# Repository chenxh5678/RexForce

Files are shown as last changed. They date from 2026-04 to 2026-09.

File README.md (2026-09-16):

# RexForce测力主板开发说明文档

>建议用电脑浏览器打开此文档，方便下载文件

## 目录
1. [设备概述](#1-设备概述)
2. [测力传感器接线](#2-测力传感器接线)
3. [电池说明](#3-电池说明)
4. [设备操作与指示](#4-设备操作与指示)
5. [连接方式](#5-连接方式)
6. [通信协议](#6-通信协议)
7. [客户端开发指南](#7-客户端开发指南)
8. [归零校准操作](#8-归零校准操作)
9. [注意事项](#9-注意事项)
10. [主板尺寸图](#10-主板尺寸图)
11. [应用程序](#11-应用程序)
12. [示例：测力台采购组装教程](测力台采购装配/README.md)
13. [成品测力台、测力计购买](#13-成品测力台测力计购买)
---

## 1. 设备概述
### 1.1 设备定义
RexForce 测力主板是一款用于测力采集的控制主板，可连接各类测力传感器，用于制造运动测力台、肌力测试仪、力量评估设备、康复评估设备、平衡测试平台等运动与康复类设备，以及工业测力计、拉压力测试机、吊装测力装置、工装夹具测力装置、智能称重终端等工业类设备。

### 1.2 功能说明
设备支持 **BLE 蓝牙** 连接和**额外串口模块**有线连接，支持手机、平板、带蓝牙功能的电脑等客户端接入，并以 **1000 Hz** 采样速率实时输出重量数据，适用于测力采集、数据显示与无线传输等应用场景。

### 1.3 工作模式
设备支持以下工作模式：
- **单机模式**：仅发送主设备重量数据。
- **双机模式**：将有线连接的主设备与副设备的重量数据合并发送。

### 1.4 主板参数
| 项目 | 参数 |
| --- | --- |
| 型号 | RexForce |
| 无线连接 | BLE 蓝牙 |
| 有线连接 | 外接额外串口模块 |
| 通讯协议 | BLE GATT + 私有应用层数据协议 |
| 采样速率 | 1000 Hz |
| 支持模式 | 单机模式、双机模式 |
| 适配传感器 | 四线全桥应变式测力传感器 |
| 测量范围 | ±3276 kg（拉力、压力） |
| 数据分辨率 | 0.1 kg |
| ADC 分辨率 | 24 位 |
| 测量精度 | 与所配传感器、机械结构及标定结果有关 |
| 通讯距离 | 10 ~ 50 m（与现场环境及客户端设备有关） |
| 工作温度范围 | -40℃ ~ 85℃（视整机配置与使用环境而定） |
| 电池类型 | 3.7 V 可充电锂电池 |
| 运行功耗 | 0.4 W |
| 传感器接口 | 插拔式 3.81 mm 接线端子 |

<p align="center">
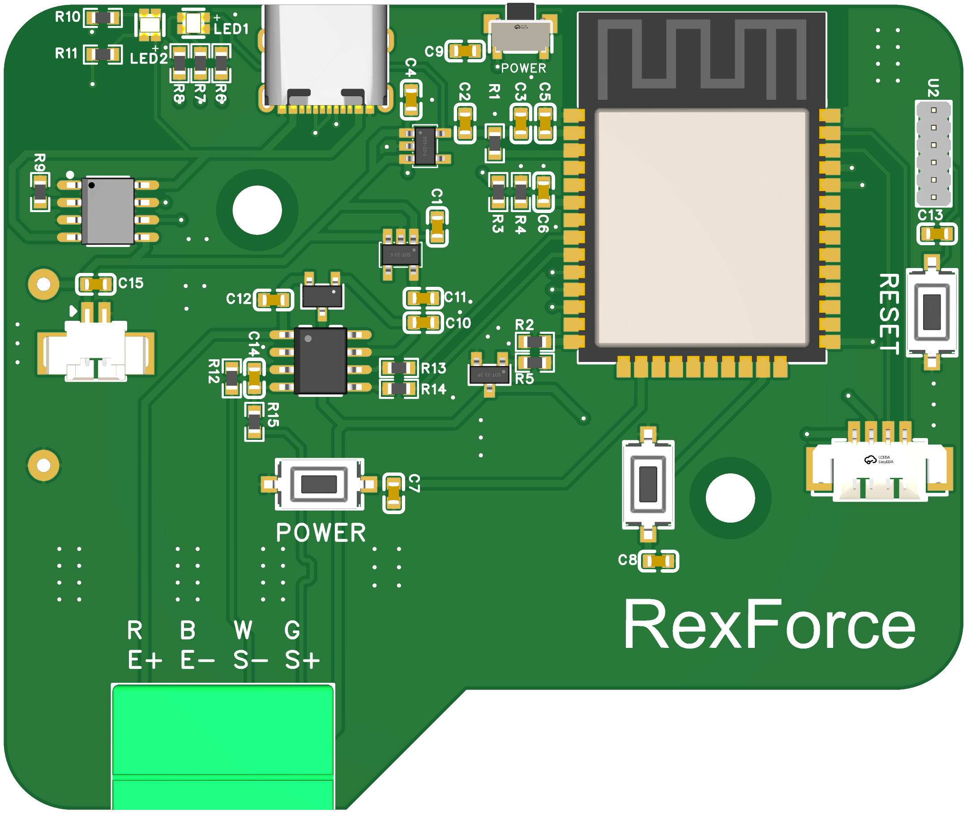
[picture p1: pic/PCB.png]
  
</p>

---

## 2. 测力传感器接线
### 2.1 适用传感器类型
主板适用于 **四线全桥应变式测力传感器**，接口定义为 `E+`、`E-`、`S+`、`S-`。

<sub>部分传感器带屏蔽线（5 线制），其中屏蔽线不接入 `E+`、`E-`、`S+`、`S-` 端子。</sub>

半桥传感器应先通过桥路补偿或加秤板转换为标准四线桥式输出后，再接入主板。

<p align="center">
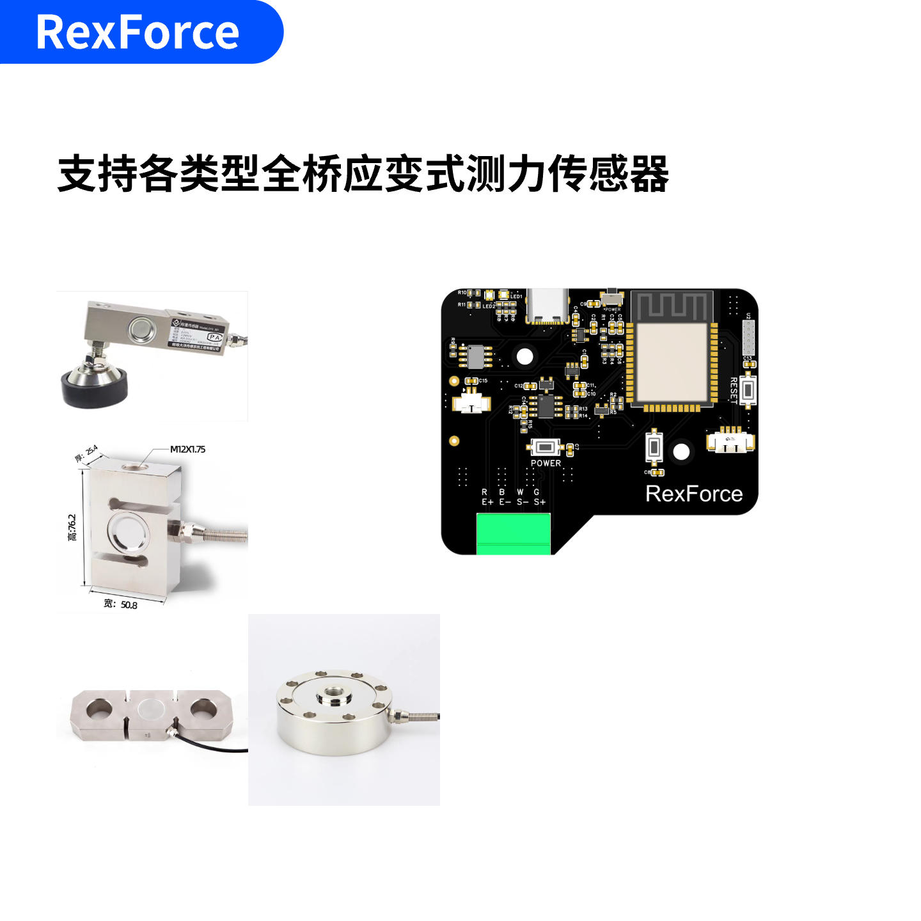
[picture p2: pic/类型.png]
  
</p>

### 2.2 接线端子定义
测力传感器接线端子共 4 个，定义如下：

| 端子 | 说明 |
| --- | --- |
| `E+` | 激励正 |
| `E-` | 激励负 |
| `S+` | 信号正 |
| `S-` | 信号负 |

接线时，应将传感器对应引线分别接入 `E+`、`E-`、`S+`、`S-` 端子。

### 2.3 多个测力传感器接入
支持多个相同传感器并联接入同一块主板。

例如：将 4 个测力传感器安装于金属板四角，并联接入一块主板，组成测力台。

并联接入时，各传感器端子定义应保持一致：

- 所有 `E+` 并接至主板 `E+`
- 所有 `E-` 并接至主板 `E-`
- 所有 `S+` 并接至主板 `S+`
- 所有 `S-` 并接至主板 `S-`

<p align="center">
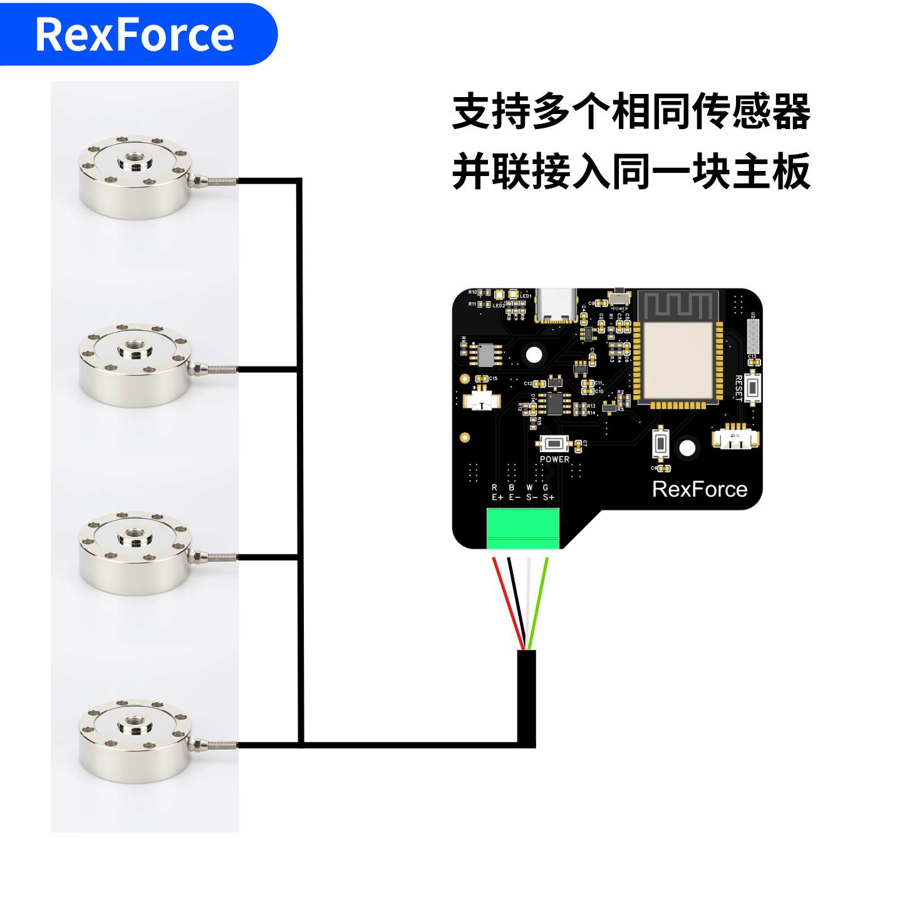
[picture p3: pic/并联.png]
  
</p>

---

## 3. 电池说明
设备使用 **3.7 V 可充电锂电池** 供电。

电池接口必须使用 **1.25 红黑插头**，不得使用其他规格插头直接接入。

接线前应确认电池极性与插头规格一致。

### 3.1 充电说明
设备内置锂电池充电管理电路。

典型充电电流约为 **1000 mA**。

充电输入建议使用稳定的 **5 V** 电源。

为保证电池寿命与充电安全，建议配套使用单节 **3.7 V 锂电池**，并避免在高温、受压、破损或进水环境下充电。

设备运行过程中如同时充电，实际充电电流可能因系统负载而下降，充满时间也会相应延长。

---

## 4. 设备操作与指示
### 4.1 开关机
#### 开机
长按电源键，绿灯亮起后设备启动。启动后设备自动归零，归零期间请勿在测量面放置重物。

#### 关机
长按电源键，LED 红灯亮起后熄灭，设备关机。

### 4.2 按键操作
#### 电源键（功能键）
| 操作 | 效果 |
| --- | --- |
| 短按 | 切换连接模式：BLE ↔ 有线 |
| 长按 | 开关机 |

- BLE 已连接时，短按切换无效，应先断开蓝牙连接。
- 切换至 BLE 模式时，LED 蓝色闪烁 1 秒；切换至有线模式时，LED 青色闪烁 1 秒。确认后恢复显示电量状态。
- 2 秒内重复短按无效（防抖）。

#### 复位键
复位键用于设备复位。

### 4.3 电量显示
| 电量状态 | LED 颜色 |
| --- | --- |
| 充足 | 绿色 |
| 中等 | 黄色 |
| 低 | 红色 |

---

## 5. 连接方式
### 5.1 BLE 蓝牙连接（默认）
- 设备上电后自动广播 BLE，名称格式为 `Force-XXXX`，其中 `XXXX` 为设备唯一 ID 后 4 位。
- 客户端扫描并连接对应设备，无需配对码。
- 设备处于待连接状态时，LED 以 500 ms 间隔闪烁。
- 连接建立后，设备立即开始推送数据，LED 切换为常亮状态。
- 建议连接后协商 MTU ≥ 244 字节。

### 5.2 有线连接
- 有线模式可用于主设备与副设备之间的数据传输，也支持连接串口模块直接连接电脑客户端。
- 使用双 Type-C 数据线连接两台设备，其中一台切换为有线模式作为副设备，另一台保持 BLE 模式作为主设备。
- 主设备建立蓝牙连接后自动检测副设备连接状态；检测到副设备后，自动进入双机模式。
- 双机模式下，副设备将重量数据发送给主设备；主设备整合两设备数据后，推送给客户端，客户端按 `6.2` 节格式解析即可。
- 切换至有线模式后，LED 青色闪烁 1 秒确认，随后切换为常亮状态。
- 串口参数：波特率 `921600 bps`，格式 `8N1`。

---

## 6. 通信协议
### 6.1 BLE GATT 服务信息
| 项目 | UUID |
| --- | --- |
| 服务 UUID | `0000FFE5-0000-1000-8000-00805F9A34FB` |
| TX 特征（设备→客户端，Notify） | `0000FFE4-0000-1000-8000-00805F9A34FB` |
| RX 特征（客户端→设备，Write） | `0000FFE9-0000-1000-8000-00805F9A34FB` |

---

### 6.2 设备 → 客户端：数据帧格式
#### BLE 模式：固定 244 字节帧
```plain
字节位置    长度    含义
[0]         1      帧头 SLAVE，固定 0x01
[1]         1      功能码 FUNC，见下表
[2~3]       2      首个数据点时间戳（大端，单位 ms，对 65535 取余循环）
[4~243]     240    重量数据区
```

##### 功能码（FUNC）
| FUNC 值 | 模式 | 数据区含义 |
| --- | --- | --- |
| `0x03` | 单机 | 240 字节 = 80 个数据点 × 3 字节/点 |
| `0x05` | 双机 | 240 字节 = 40 组数据 × 6 字节/组（主设备 3 字节 + 副设备 3 字节） |

##### 单机模式数据区（FUNC = 0x03）
每个重量点占 3 字节：

```plain
[HIGH_BYTE] [LOW_BYTE] [CHECKSUM]
```

+ `HIGH_BYTE + LOW_BYTE`：大端有符号 16 位整数，值 = 重量(kg) × 10。
+ 数值正负表示受力方向；通常可对应压力与拉力，具体含义取决于传感器类型及安装方式。
+ 示例：`0x00 0x7B` → 123 → 12.3 kg；`0xFF 0x85` → -123 → -12.3 kg。
+ 表示范围：-3276.8 ~ +3276.7 kg。
+ `CHECKSUM = (HIGH_BYTE + LOW_BYTE) & 0xFF`，校验失败时该点应丢弃。

**Python 解码示例：**

```python
def decode_point(high, low, checksum):
    if (high + low) & 0xFF != checksum:
        return None  # 校验失败，丢弃
    val = (high << 8) | low
    if val >= 32768:
        val -= 65536  # 有符号处理
    return val / 10.0  # 单位：kg
```

##### 双机模式数据区（FUNC = 0x05）
每组数据占 6 字节，分别表示主设备和副设备各 1 个重量点：

```plain
[主设备 HIGH] [主设备 LOW] [主设备 CHECKSUM] [副设备 HIGH] [副设备 LOW] [副设备 CHECKSUM]
```

+ 前 3 字节为主设备重量，解码方式同上。
+ 后 3 字节为副设备重量，解码方式同上。
+ 副设备数据若为 `0x00 0x00 0x00`，其解码结果为 0.0 kg，不应直接视为无数据。
+ 合力 = 主设备重量 + 副设备重量。

##### 数据帧示例

###### 示例 1：单机模式帧头 + 前 3 个数据点

```plain
01 03 12 34  00 7B 7B  FF 85 84  00 11 11  ...（后续补满 240 字节数据区）
```

说明：

+ `01`：帧头 `SLAVE = 0x01`
+ `03`：功能码 `FUNC = 0x03`，表示单机模式
+ `12 34`：首个数据点时间戳 = `0x1234` = 4660 ms
+ 第 1 个点 `00 7B 7B`：原始值 `0x007B` = 123，重量 12.3 kg，校验正确
+ 第 2 个点 `FF 85 84`：原始值 `0xFF85` = -123，重量 -12.3 kg，校验正确
+ 第 3 个点 `00 11 11`：原始值 `0x0011` = 17，重量 1.7 kg，校验正确

###### 示例 2：双机模式帧头 + 前 2 组数据

```plain
01 05 00 50  00 3D 3D  00 1B 1B  FF C9 C8  00 09 09  ...（后续补满 240 字节数据区）
```

说明：

+ `01`：帧头 `SLAVE = 0x01`
+ `05`：功能码 `FUNC = 0x05`，表示双机模式
+ `00 50`：首个数据点时间戳 = `0x0050` = 80 ms
+ 第 1 组 `00 3D 3D  00 1B 1B`：主设备 6.1 kg，副设备 2.7 kg，合力 8.8 kg
+ 第 2 组 `FF C9 C8  00 09 09`：主设备 -5.5 kg，副设备 0.9 kg，合力 -4.6 kg

###### 示例 3：校验失败的数据点

```plain
00 7B 7C
```

+ 该点原始值为 `0x007B`，即 123 → 12.3 kg。
+ 正确校验应为 `(0x00 + 0x7B) & 0xFF = 0x7B`。
+ 实际收到 `0x7C`，说明校验失败，客户端应丢弃该点。

##### 时间戳说明
+ 字节 `[2~3]` 为该帧第一个数据点的采集时间戳（ms），大端无符号 16 位。
+ 取值范围为 0~65534，对 65535 取余循环，约每 65 秒归零一次。
+ 相邻帧时间戳理论差值约为 80 ms，可用于检测丢帧。

---

### 6.3 客户端 → 设备：控制指令
通过 **BLE RX 特征 Write** 发送以下字节序列：

| 指令 | 字节序列 | 长度 | 说明 |
| --- | --- | --- | --- |
| 恢复默认比例系数 | `0x54 0xF8` | 2 | 将比例系数恢复为默认值 |
| 请求温度原始值 | `0x54 0xDD` | 2 | 设备回传温度响应（见 6.4 节） |
| 主动断开 BLE 连接 | `0x54 0xDE` | 2 | 设备主动断开当前 BLE 连接，并回到可广播状态 |
| 发送校准因子 | `0x54 0xAA` + 4 字节大端整数 | 6 | 校准比例系数 |

#### 主动断开指令
向 BLE RX 特征写入 `0x54 0xDE` 后，设备会主动断开当前 BLE 连接。

适用场景：

+ 远程触发设备断连。
+ 切换设备、重新扫描或重连测试前，使设备先回到待连接状态。

发送成功后：

+ 当前 BLE 连接断开。
+ 设备重新进入广播状态，可再次扫描并重连。

#### 校准因子指令
校准因子 = 当前测量值 ÷ 标准砝码值；放大 10000 倍后，以 4 字节大端无符号整数发送。

**示例**：标准砝码值 5.00 kg，当前测量值 5.23 kg：

```python
import struct
standard_weight_kg = 5.00
measured_kg = 5.23
factor = measured_kg / standard_weight_kg   # ≈ 1.046
factor_int = int(round(factor * 10000))     # = 10460
cmd = bytes([0x54, 0xAA]) + struct.pack('>I', factor_int)
# 发送 cmd（共 6 字节）到 BLE RX 特征
```

设备收到后立即更新比例系数并持久化保存，无需重启。

---

### 6.4 设备 → 客户端：温度响应帧
客户端发送温度请求指令后，设备通过 **TX 特征 Notify** 回传：

```plain
[0x54] [0xDD] [B3] [B2] [B1] [B0]   共 6 字节
```

+ `B3~B0` 为温度原始值，采用大端有符号 32 位整数。

```python
import struct
raw_temp = struct.unpack('>i', bytes([B3, B2, B1, B0]))[0]
```

温度需经单点校正后换算，公式如下：

```plain
T_B(°C) = Yb × (273.15 + T_A) / Ya - 273.15
```

| 变量 | 含义 |
| --- | --- |
| `T_A` | 已知参考温度点（°C） |
| `Ya` | 在 `T_A` 下读取的原始码值 |
| `Yb` | 待测温度点读取的原始码值 |
| `T_B` | 换算后的实际温度（°C） |

使用方法：

1. 在已知温度 `T_A` 下读取一次原始值 `Ya`，作为校正基准。
2. 后续读取原始值 `Yb` 后，按公式计算实际温度。

**Python 示例：**

```python
# 校正基准（在已知温度 T_A=25°C 时读取一次 Ya）
T_A = 25.0
Ya  = 基准码值  # 在 25°C 下实测读取

# 后续测量
Yb  = raw_temp  # 当前读取的原始值
T_B = Yb * (273.15 + T_A) / Ya - 273.15
print(f"温度: {T_B:.2f} °C")
```

---

## 7. 客户端开发指南
### 7.1 BLE 连接示例（Python）
```python
# 推荐使用 bleak 库（跨平台）
# pip install bleak

import asyncio
from bleak import BleakScanner, BleakClient

TX_UUID = "0000FFE4-0000-1000-8000-00805F9A34FB"  # Notify（接收数据）
RX_UUID = "0000FFE9-0000-1000-8000-00805F9A34FB"  # Write（发送指令）

async def main():
    devices = await BleakScanner.discover(timeout=5.0)
    target = next((d for d in devices if d.name and d.name.startswith("Force-")), None)
    if not target:
        print("未找到设备")
        return

    async with BleakClient(target.address) as client:
        print(f"已连接: {target.name}")

        buf = bytearray()

        def on_notify(sender, data):
            buf.extend(data)
            while len(buf) >= 244:
                if buf[0] == 0x01 and buf[1] in (0x03, 0x05):
                    frame = bytes(buf[:244])
                    del buf[:244]
                    parse_frame(frame)
                else:
                    del buf[0]

        await client.start_notify(TX_UUID, on_notify)
        await asyncio.sleep(10)
        await client.stop_notify(TX_UUID)

asyncio.run(main())
```

### 7.2 完整帧解析示例
```python
FRAME_LEN      = 244
DATA_FIELD_LEN = 240

def decode_point(high, low, checksum):
    """解码 3 字节重量点，校验失败返回 None。"""
    if (high + low) & 0xFF != checksum:
        return None
    val = (high << 8) | low
    if val >= 32768:
        val -= 65536
    return val / 10.0

def parse_frame(frame: bytes):
    slave = frame[0]   # 0x01
    func  = frame[1]   # 0x03 单机 / 0x05 双机
    ts_ms = (frame[2] << 8) | frame[3]  # 首样时间戳 ms

    if func == 0x03:  # 单机模式
        for i in range(0, DATA_FIELD_LEN, 3):
            w = decode_point(frame[4+i], frame[5+i], frame[6+i])
            if w is not None:
                print(f"  ts={ts_ms}ms  weight={w:.1f} kg")

    elif func == 0x05:  # 双机模式
        for i in range(0, DATA_FIELD_LEN, 6):
            local = decode_point(frame[4+i], frame[5+i], frame[6+i])
            remote = decode_point(frame[7+i], frame[8+i], frame[9+i])
            if local is not None and remote is not None:
                combined = local + remote
                print(f"  ts={ts_ms}ms  主设备={local:.1f}  副设备={remote:.1f}  合力={combined:.1f} kg")
```

### 7.3 指令发送示例
```python
import struct

# 恢复默认比例系数
await client.write_gatt_char(RX_UUID, bytes([0x54, 0xF8]))

# 请求温度原始值
await client.write_gatt_char(RX_UUID, bytes([0x54, 0xDD]))

# 主动断开 BLE 连接
await client.write_gatt_char(RX_UUID, bytes([0x54, 0xDE]))

# 发送校准因子（标准砝码值 standard_weight_kg，当前测量值 measured_kg）
standard_weight_kg = 5.00
measured_kg = 5.23
factor_int = int(round((measured_kg / standard_weight_kg) * 10000))
cmd = bytes([0x54, 0xAA]) + struct.pack('>I', factor_int)
await client.write_gatt_char(RX_UUID, cmd)
```

---

## 8. 归零校准操作
制作好测力设备后，必须先使用实际使用场景重量的**精确砝码**进行校准。

1. 完成设备安装与传感器接线后，确认机械结构已固定，测量面无额外载荷。
2. 给设备上电，等待主板自动归零完成；归零期间请勿在测量面放置重物。
3. 选择稳定、精确的标准砝码，且砝码重量应尽量接近设备的实际使用区间，不宜过小。
4. 例如：如设备平时测量范围在 `0 ~ 30 kg`，优先使用 `10 kg` 或 `20 kg` 标准砝码进行校准；如仅使用 `1 kg` 小砝码，分辨率影响和误差更容易被放大。
5. 将标准砝码放置到规定受力位置，读取当前显示值，按“**读取显示值 ÷ 标准砝码值**”计算校准因子，并按 `6.3` 节的方法发送校准命令。
6. 建议完成单点校准后，再进行 `2 ~ 3` 个点的加载验证。例如：归零后依次测试 `5 kg`、`10 kg`、`20 kg`，检查各点显示值是否均接近真实值。
7. 如出现某一个点显示准确、而其他点偏差明显较大的情况，则问题可能不只是比例系数，还可能与机械结构受力不均、传感器非线性、安装方式或程序滤波 / 清零逻辑有关。
8. 校准完成后，移除砝码并再次检查空载零点及加载显示是否正常。

---

## 9. 注意事项
1. **MTU 协商**：建议连接后协商 MTU ≥ 244 字节。设备默认 MTU 为 400。
2. **校验处理**：每个数据点均包含 1 字节校验和；校验失败时应直接丢弃，不应补零。
3. **时间戳环绕**：时间戳约每 65 秒归零一次，客户端应处理环绕。
4. **双机 0 值**：副设备三字节为 `0x00 0x00 0x00` 时，其解码结果为 `0.0 kg`，不应直接视为无数据。
5. **开机归零**：开机自动归零期间请勿放置重物，以免零点偏移。
6. **模式切换限制**：BLE 已连接时不能切换模式，需先断开蓝牙连接。
7. **设备命名**：BLE 广播名称格式为 `Force-XXXX`，其中 `XXXX` 为芯片 ID 后 4 位。
8. **校准生效**：发送校准因子后立即生效，并自动保存。
9. **有线模式范围**：有线模式用于两台 RexForce 主板互联，也支持有线接串口模块连接电脑客户端。

---

## 10. 主板尺寸图

<p align="center">
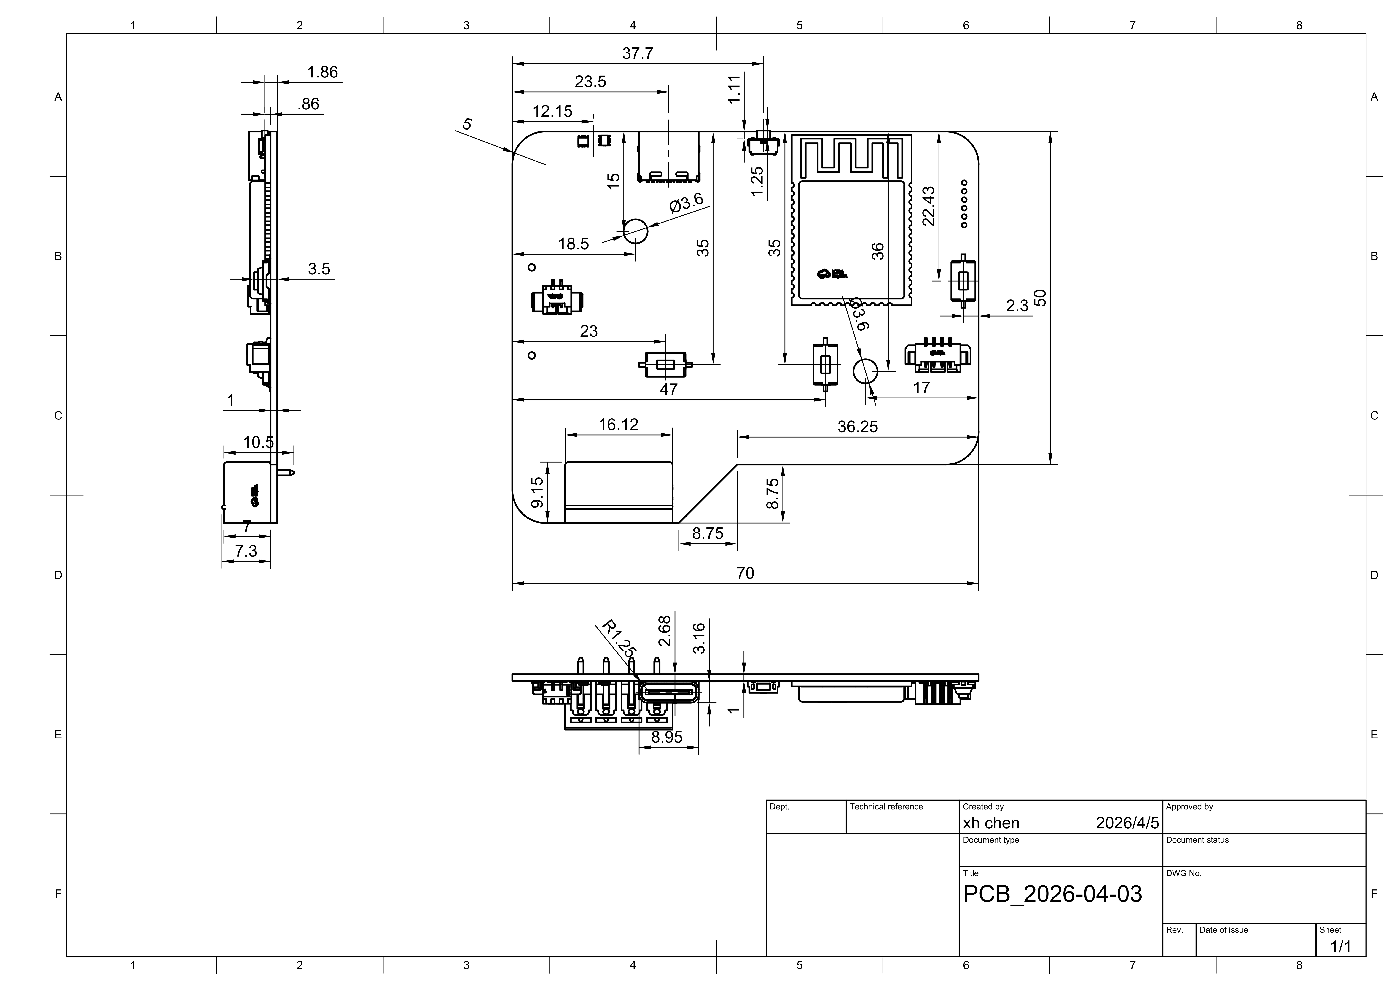
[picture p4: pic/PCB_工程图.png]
  
</p>

---

## 11. 应用程序

### 11.1 示例程序
文档中提供的示例 Python、html（网页）、ios 程序可作为上位机接入参考，用于演示 RexForce 测力主板的 BLE 扫描、设备连接、数据接收、帧解析及指令发送等基础开发流程，建议用网页程序例程，功能较完善。

该程序可实现以下功能：

1. 扫描并连接 `Force-XXXX` 设备。运行程序前，应确保客户端设备具备 BLE 功能，且 RexForce 主板已正常启动状态；
2. 建立连接后，接收并处理主板上传的数据，同时可发送常用控制指令，如读取温度、发送校准因子、恢复默认比例系数及断开连接；
3. 测试过程中可记录原始数据，并在测试结束后保存为 Excel 文件；
4. 可作为上位机软件开发的基础通信示例，供开发者进一步扩展数据采集、测试控制、结果显示、数据记录与业务集成等功能。

### 11.2 微信小程序：体能训练追踪Lab
`体能训练追踪Lab` 是一款可与 RexForce 测力主板配套使用的微信小程序，适用于基于本主板构建的肌力测试设备与测力台设备的数据采集、测试执行与结果查看。

根据所连接传感器数量及整机形态的不同，小程序可支持以下典型应用方式：

- **肌力测试应用**：当主板连接 **1 个拉力传感器** 时，设备可作为**肌力测力计**使用，用于开展相关肌力测试。
- **测力台应用**：当主板连接 **4 个压力传感器** 并集成为**测力台**后，可使用小程序中的测力台相关功能进行测试与数据分析。

### 11.3 开发者应用登记
欢迎用户基于 RexForce 测力主板，自行开发 App、小程序或其他相关应用。

如已完成相关应用开发，或正在开展基于本主板的应用方案设计，可将应用名称、主要功能及适用场景留言登记在此，便于后续整理与展示更多生态应用案例。

---

## 12. 示例：测力台采购装配教程

[点此查看测力台采购组装教程](测力台采购装配/README.md)

<p align="center">
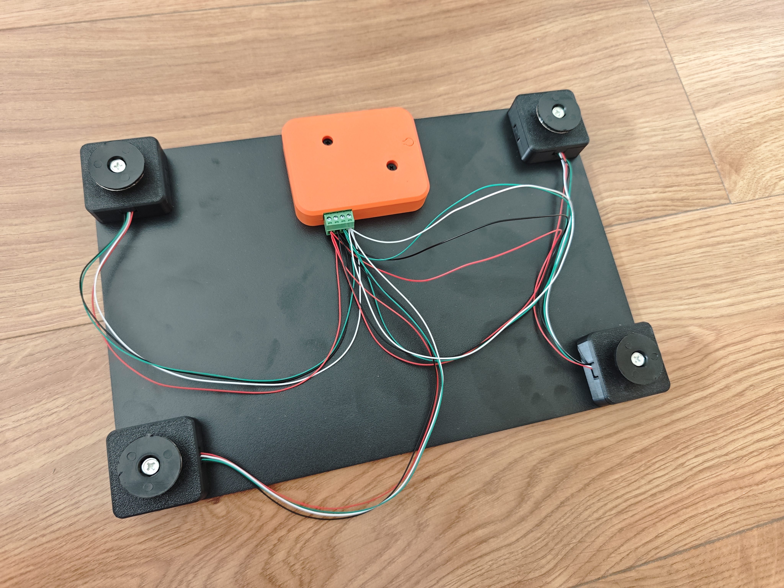
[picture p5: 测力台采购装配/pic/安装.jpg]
  
</p>

---

## 13. 成品测力台测力计购买
### 13.1 测力台
>以下为第三方销售，不是开发者，请直接与他们联系

[【淘宝】便携式测力台1000hz高频稳定采样](https://e.tb.cn/h.8IyaM3IQw8yUZtt?tk=KJogT8ycMCE) 

<p align="center">
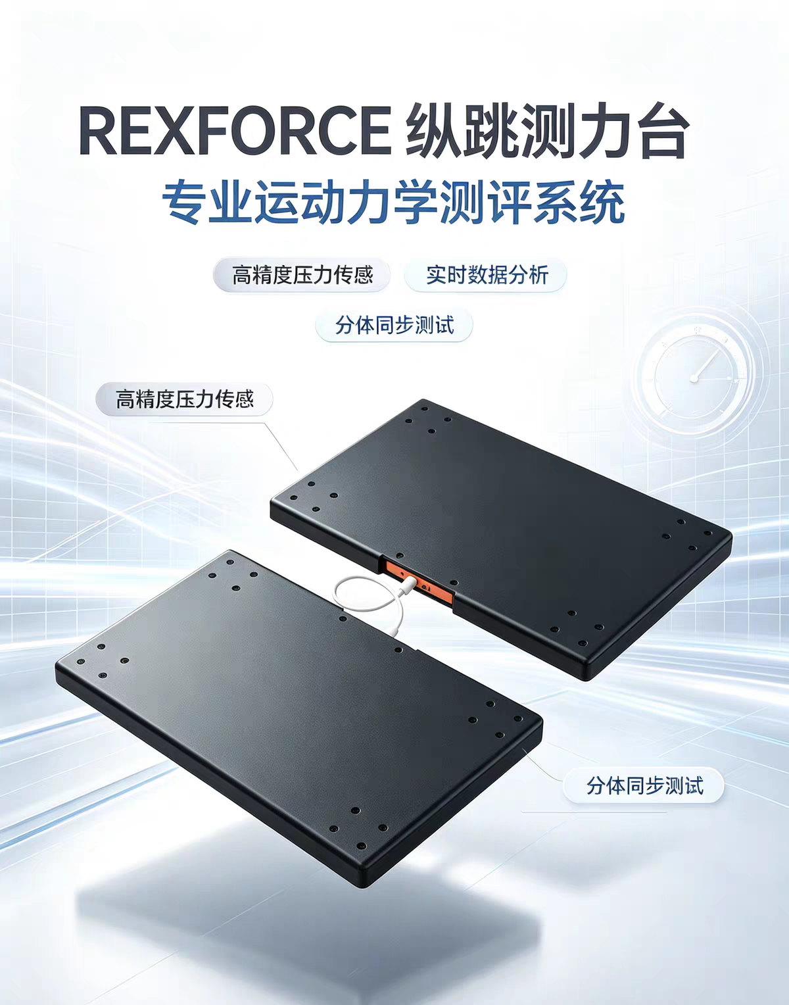
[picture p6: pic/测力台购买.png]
  
</p>

### 13.2 测力计

[【淘宝】MuscleForce肌力测力计 肌肉力量测试仪 专业运动康复评估](https://e.tb.cn/h.8jrn9edppDYU9H7?tk=XEAST14bC2i) 

<p align="center">
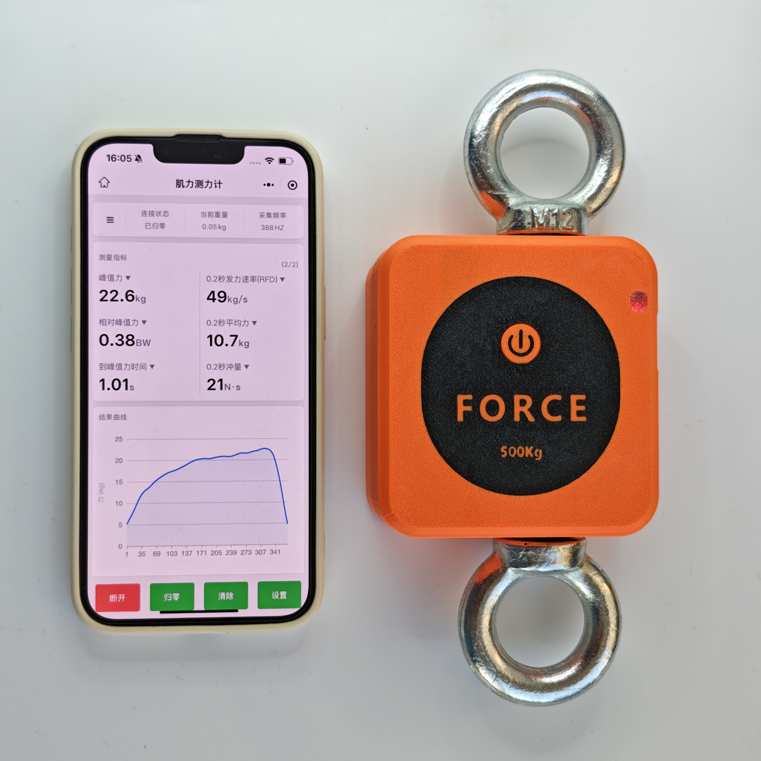
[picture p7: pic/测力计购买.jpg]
  
</p>

---

_文档版本：2026-09-16_

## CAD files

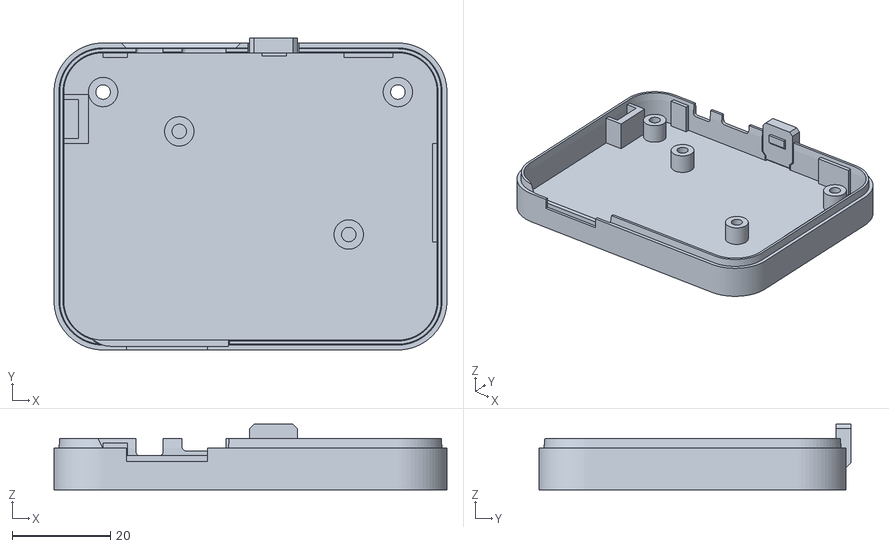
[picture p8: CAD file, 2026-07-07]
测力台采购装配/3D外壳文件/电路壳下.stl
80.0 x 63.5 x 13.4

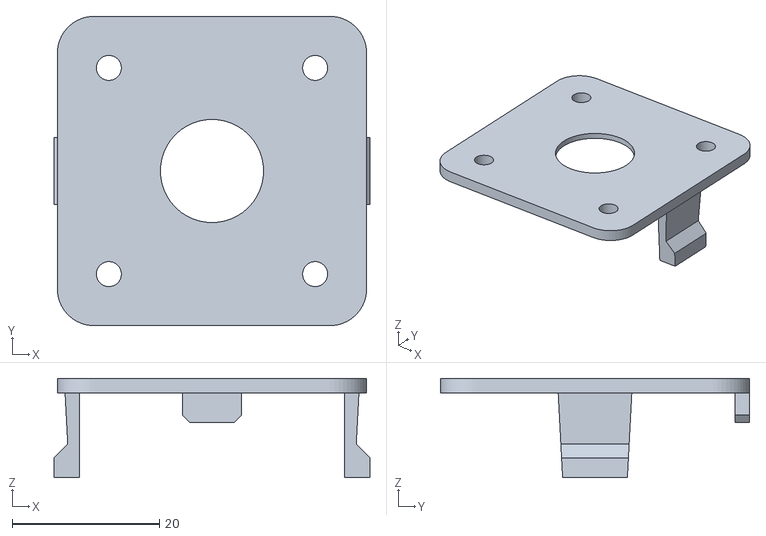
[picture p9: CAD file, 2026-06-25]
测力台采购装配/3D外壳文件/传感器外壳盖.stl
42.9 x 42.0 x 13.5

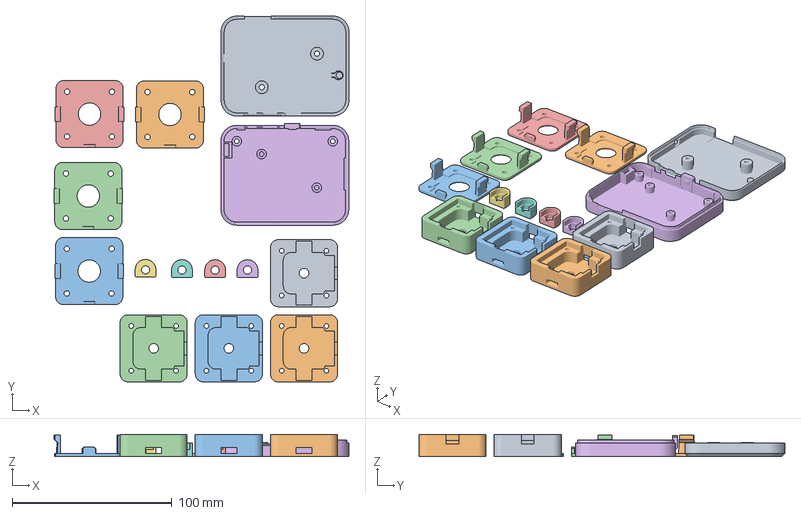
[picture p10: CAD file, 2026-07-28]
测力台采购装配/3d打印文件.3mf
184.4 x 228.7 x 14.0 mm
称脚底 - 副本.STL x 4
螺母扣.stl x 4
电路壳上.stl
传感器外壳盖.stl x 4
电路壳下.stl

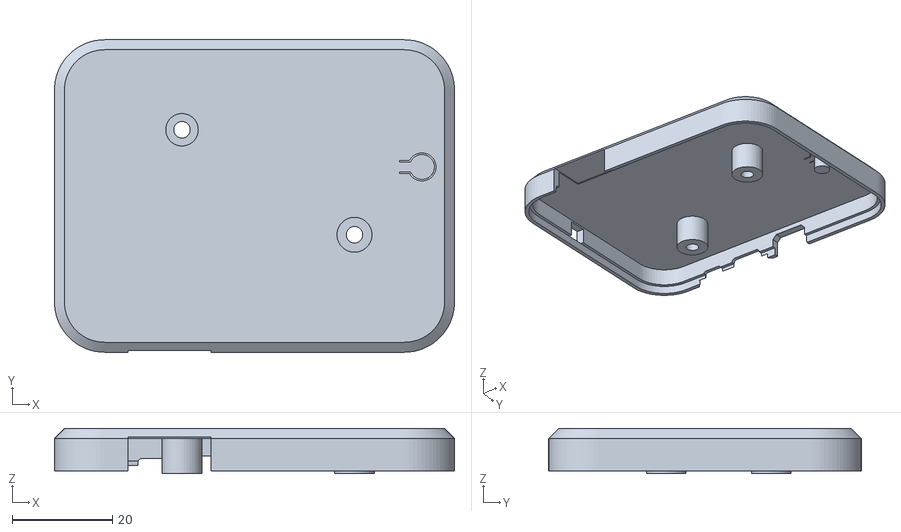
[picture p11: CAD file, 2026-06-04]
测力台采购装配/3D外壳文件/电路壳上.stl
80.0 x 62.5 x 9.00

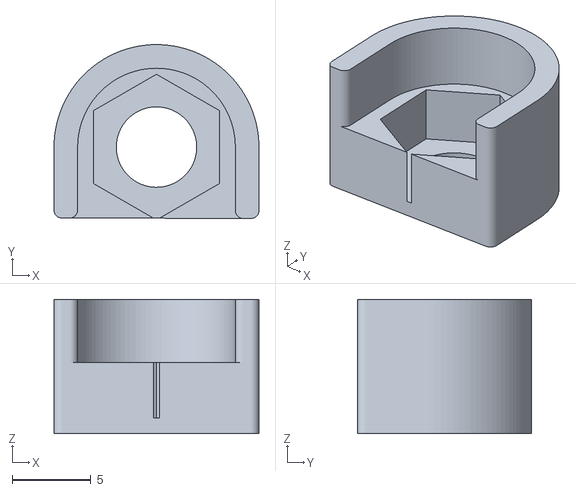
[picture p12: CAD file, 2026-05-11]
测力台采购装配/3D外壳文件/螺母扣.stl
13.0 x 11.0 x 8.50

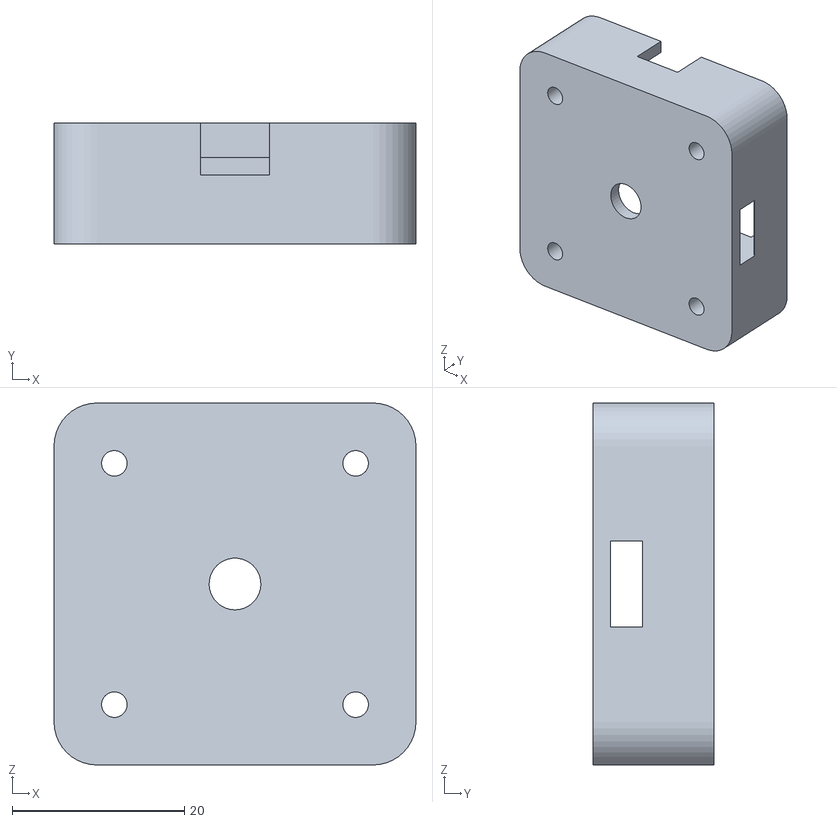
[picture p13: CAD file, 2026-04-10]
测力台采购装配/3D外壳文件/传感器外壳下.STL
42.0 x 14.0 x 42.0

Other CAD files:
测力台采购装配/350×250mm钢板定制图纸烤漆.dwg

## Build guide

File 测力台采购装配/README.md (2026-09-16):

# 基于RexForce主板的测力台零件采购与组装说明

[点击这里查看RexForce主板开发说明文档](../README.md)

[点击这里查看组装视频教程](https://www.bilibili.com/video/BV1iDtv6AEkH/?spm_id_from=333.1387.homepage.video_card.click&vd_source=62abb6fab9f91cdaa9f76e8942c84d40)

<p align="center">
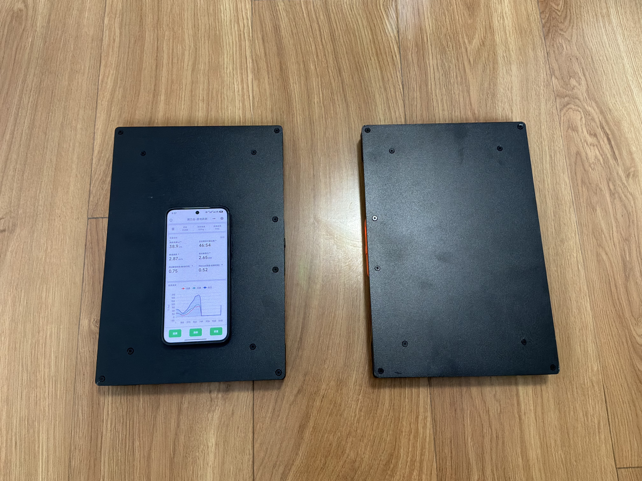
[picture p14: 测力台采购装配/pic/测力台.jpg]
  
</p>

**以下是一块测力台的零件，如果要制作两块进行双脚测试，零件数量×2即可。**

组装两个的材料大概1600

## 1 工具

### 1.1 十字螺丝刀、一字螺丝刀

[【淘宝】绿林螺丝刀套装](https://e.tb.cn/h.imDQMPqkdzBjzan?tk=mr7W540cw6q)

### 1.2 鸭嘴剥线钳

[【淘宝】德力西剥线钳](https://e.tb.cn/h.im4mGovcTXpFgY3?tk=erW6540cWMN) 

### 1.3 标准砝码（可选）

> 日常使用可以用体重代替砝码，即人站上去用体重进行校准

[ 【淘宝】标准砝码](https://e.tb.cn/h.ioBJtIZrXX8hFKA?tk=fKoD5UCPU7m)

## 2 零件

### 2.1 RexForce测力主板1个

[【淘宝】RexForce测力主板](https://e.tb.cn/h.im4tIFMHybAbLcZ?tk=U6I85407mQf) 

### 2.2 锂电池1个

[【淘宝】3.7V聚合物锂电池](https://e.tb.cn/h.im4aTgAbRC0qc8I?tk=jRqv54Zn69S) 

锂电池

### 2.3 测力传感器4个

[【淘宝】测力传感器](https://e.tb.cn/h.iJ1PV9ClVYTvE5E?tk=cuvu5ScJeLK) 

传感器1 

>单个传感器200kg量程，四个800kg。如果200kg缺货，用100kg的也可以。要跟客服确认线多长，装在钢板上长度是否足够。4个传感器必须用相同型号、量程、灵敏度等，要匹配。

### 2.4 秤脚

[【淘宝】带胶垫 28-M5×9 10套](https://e.tb.cn/h.R7ve028RES5DzhJ?tk=9AIrgZ0T8Fr) 

<p align="center">
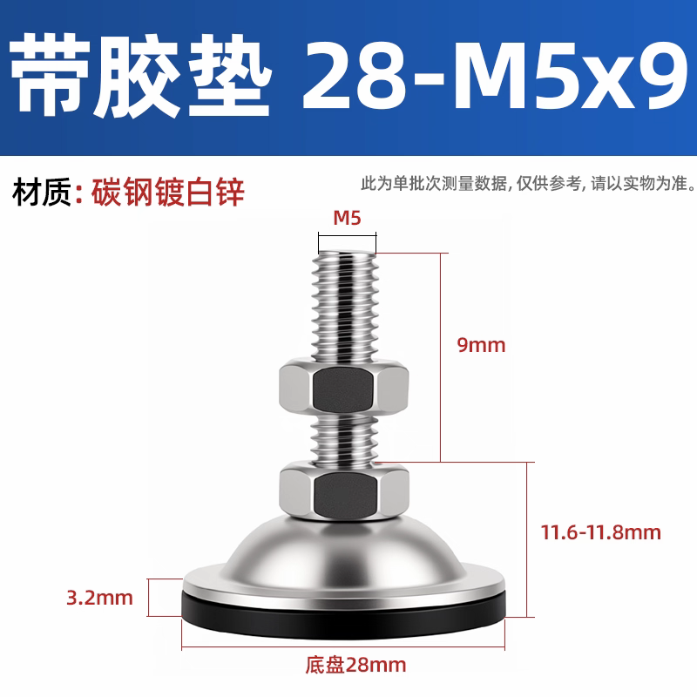
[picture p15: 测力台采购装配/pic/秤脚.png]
  
</p>

### 2.5 外壳3D打印1套

>联系淘宝客服，将下载好的 `3D打印文件.3mf` 文件发给客服，打印即可。可以联系客服自己选颜色和材料。

[【淘宝】3D打印服务](https://e.tb.cn/h.inaKN3jBCLKEbqG?tk=2rhw54ZtYiK) 

<p align="center">
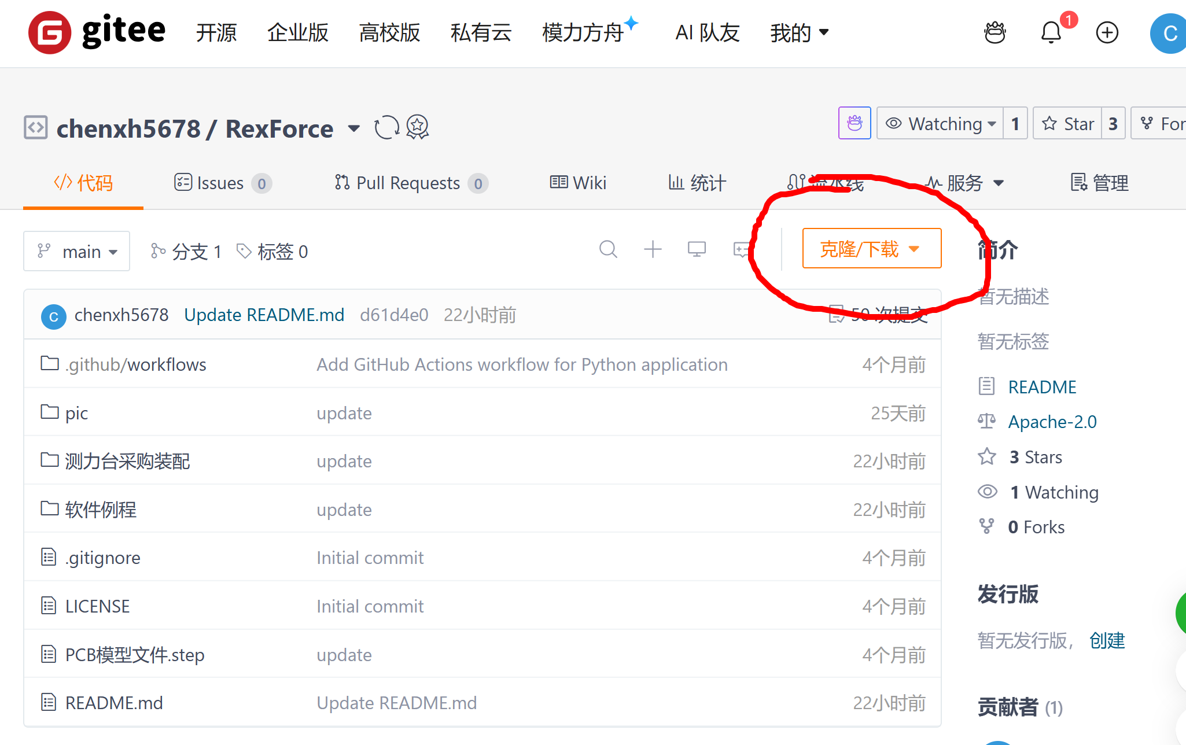
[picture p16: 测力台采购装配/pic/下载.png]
  
</p>

### 2.6 钢板定制1块

> 钢板螺丝孔图纸可以用下载的文件夹中的'350×250mm钢板定制图纸.dwg'，厚度5mm以上

[【淘宝】不锈钢板激光切割](https://e.tb.cn/h.inasCLNXotgxqqC?tk=UrEN54ZE8SY) 

### 2.7 M3螺丝2~20个

[【淘宝】M3黑色不锈钢螺丝](https://e.tb.cn/h.iOpqxURZDhgB21X?tk=pOpC540gd3P) 

螺丝

### 2.8 接线端子1个

[【淘宝】KF2EDG PCB接线端子](https://e.tb.cn/h.imfXjrMu2owpwlC?tk=r0nq540qWOY) 

端子1

### 2.9 屏蔽胶带铝箔胶带

[【淘宝】宽50MM*20米足长](https://e.tb.cn/h.RVo3PtKf2AzqXts?tk=mpx05vANGBk) 

### 2.10 双头Type-C数据线1根

[【淘宝】双Type-C数据线](https://e.tb.cn/h.iOpiUHw1WF56L72?tk=ZHzF54ZzYl2) 

数据线

> 用来连接两个测力台，只有一个测力台可不用数据线。

### 2.11 充电器1个（可选）

[【淘宝】PD5V1A慢充头 C口](https://e.tb.cn/h.8URQUFbLXy8JXVJ?tk=6W0ngBd6Cdv) 

### 2.12 串口模块1个（可选）

> 用于有线连接电脑使用，数据传输更稳定更快，只连蓝牙使用不需要串口模块

[【淘宝】串口模块rexforce测力台有线连接电脑](https://e.tb.cn/h.89pQIGLGLaeGpYd?tk=PlstTWyI0Gy) 

---

## 3 装配
### 3.1 传感器剥线
用鸭嘴钳将所有测力传感器的四根线末端剥出约1cm长的金属线.
<p align="center">
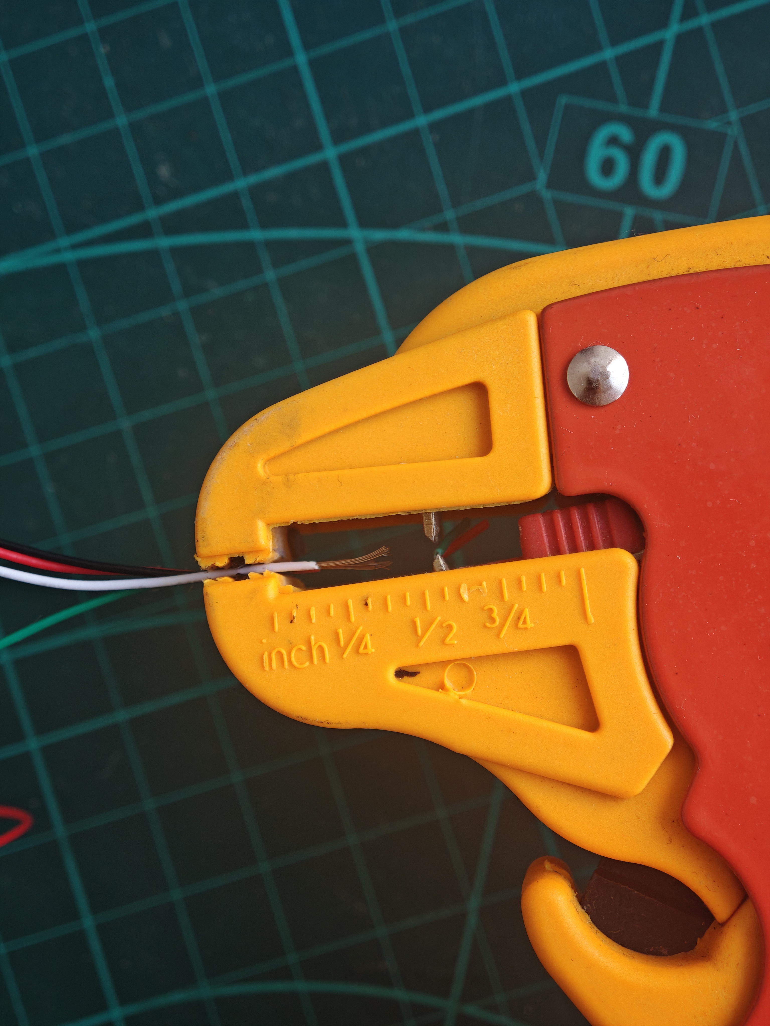
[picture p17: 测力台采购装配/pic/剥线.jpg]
剥线
  
</p>
然后将相同颜色的金属线部分拧到一起，拧好后像图中平直，勿弯折回勾等形状
<p align="center">
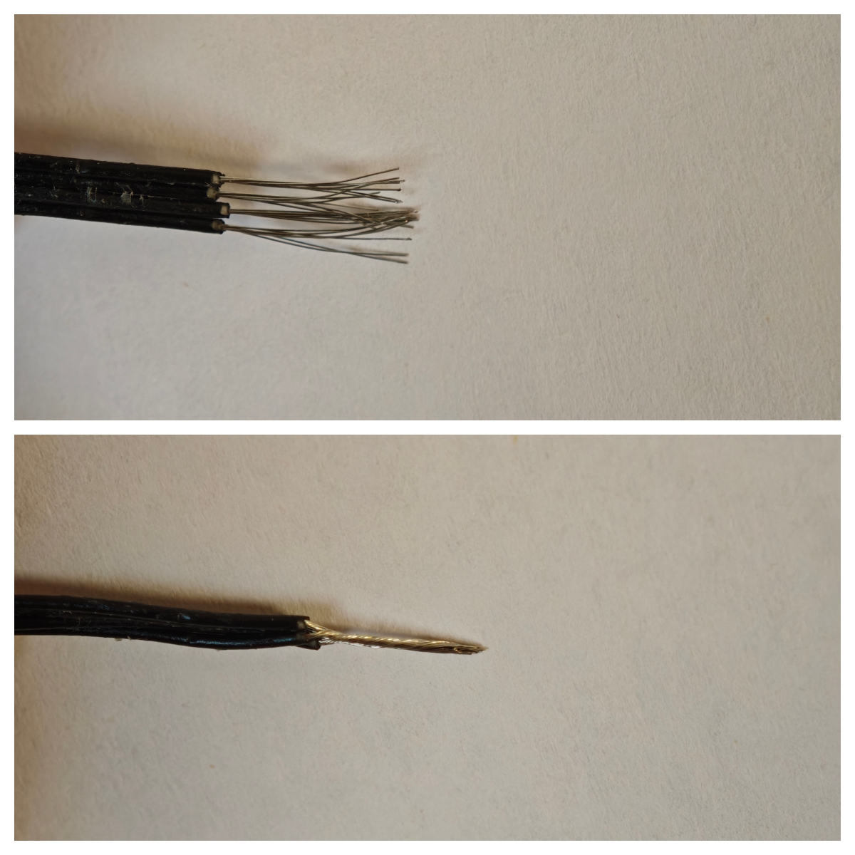
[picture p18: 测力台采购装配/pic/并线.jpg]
  
</p>
最后按红、黑、绿、白（或红、黑、白、绿）顺序插到接线端子里，用螺丝刀拧紧固定好。

>绿线、白线位置影响测力的方向，数值正或负，根据实际传感器情况进行调整

<p align="center">
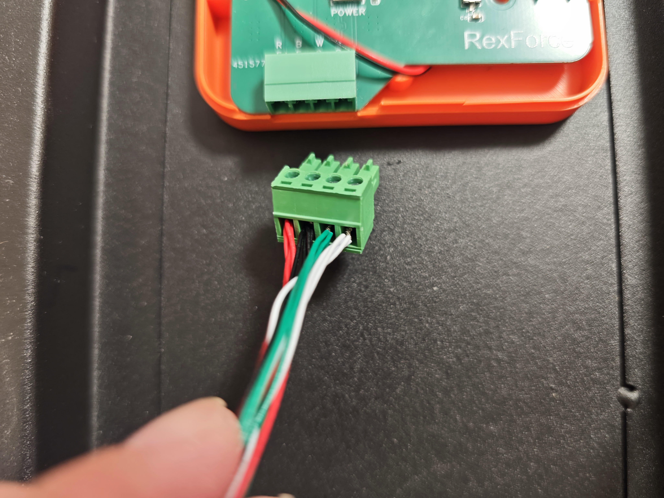
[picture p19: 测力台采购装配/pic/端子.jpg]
  
</p>

### 3.2 安装
如图插电池，插接线端子，装外壳。

<p align="center">
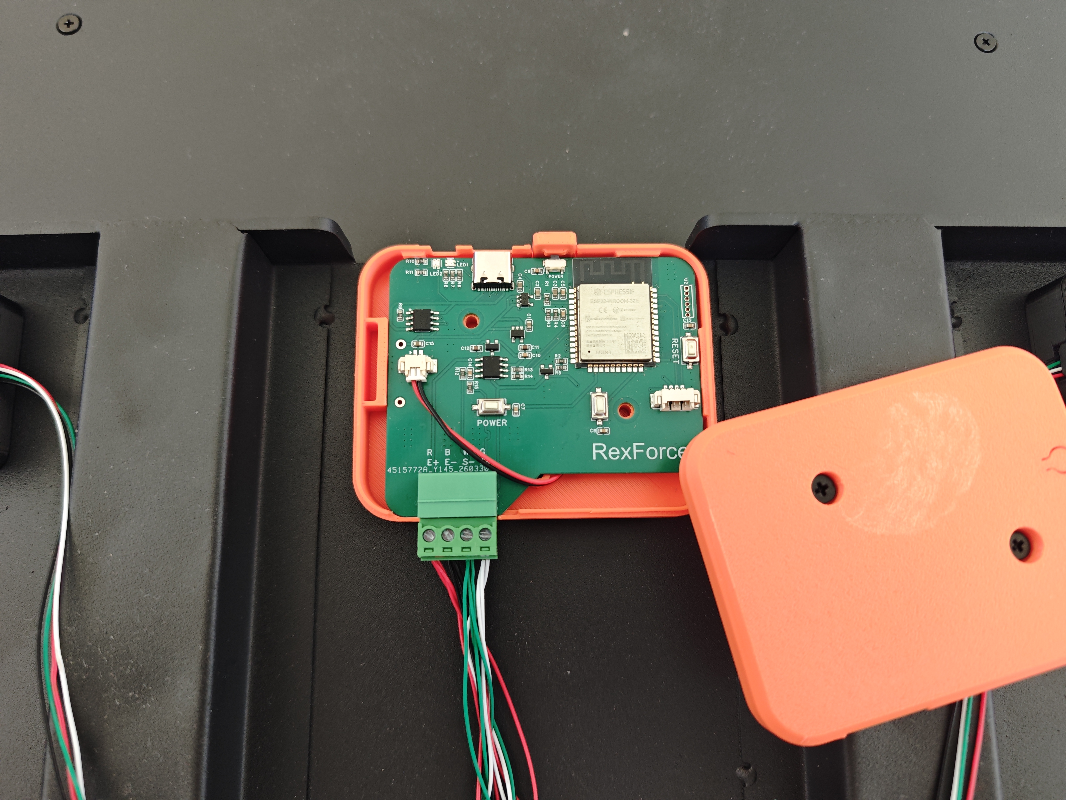
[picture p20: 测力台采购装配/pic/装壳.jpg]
  
</p>

秤脚加上盖子后，加螺母扣拧到传感器上。（图中为方便演示没加盖子）

<p align="center">
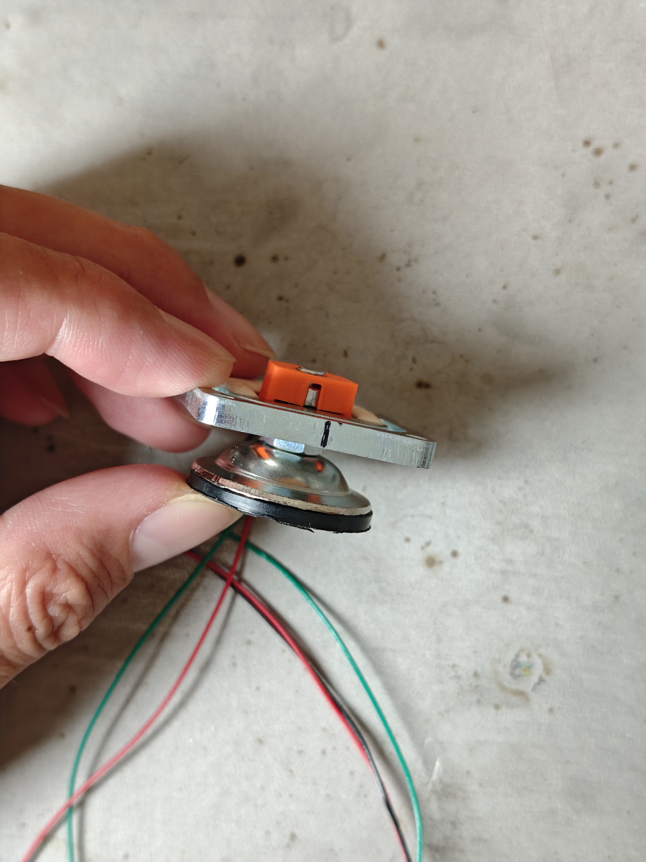
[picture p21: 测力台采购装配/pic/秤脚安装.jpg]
  
</p>

### 3.3 装钢板
用螺丝把四个传感器拧到钢板四角，然后将主机固定到钢板底部边缘。

> 
<p align="center">
  RexForce 主板示意图
</p>

### 3.4 贴屏蔽胶带
用屏蔽胶带将传感器的线贴到钢板上，将线盖严充分屏蔽外界电磁干扰
<p align="center">
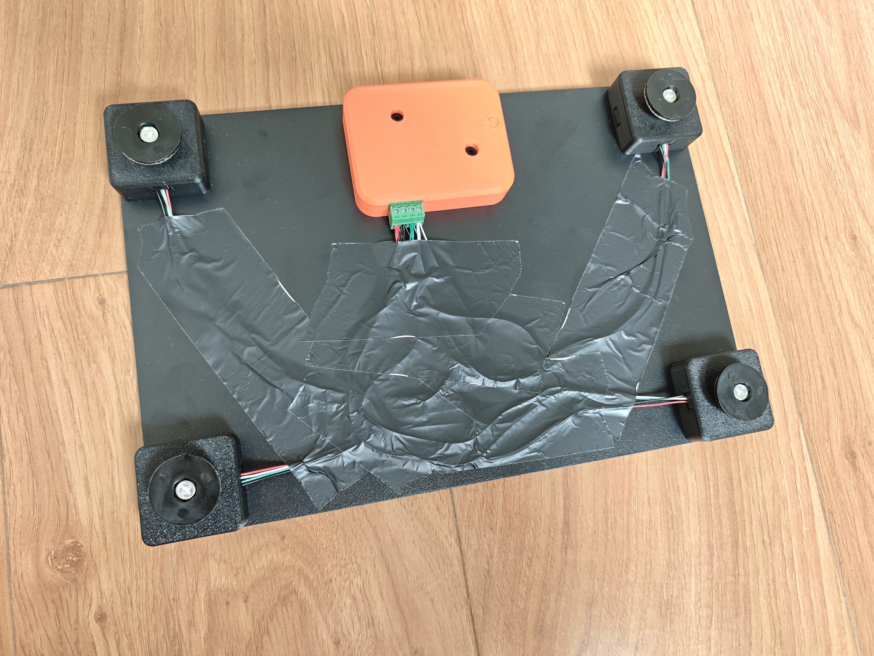
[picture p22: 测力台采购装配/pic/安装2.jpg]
  
</p>

## 4 微信小程序
装配完成后，软件能正常读取重量数据后，如果发现称重与体重不一致，就用体重或精确砝码进行**校准标定**，可以用例程或微信小程序进行校准标定操作。

>详情查看《RexForce测力主板开发说明文档》8. 归零校准操作

开机连接微信小程序《体能训练追踪Lab》，可以进行跳跃测试、等长肌力测试等。

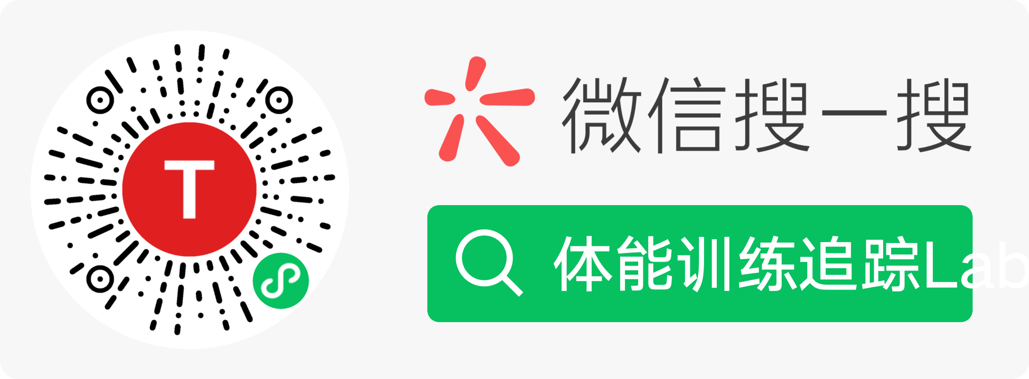
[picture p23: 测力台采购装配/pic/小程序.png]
小程序


## 5 销售问题
鼓励大家自己贴牌销售，无需告知开发者。

>如销售产生纠纷，需自行担责

在购买电路板时可联系商家修改设备BLE名称，让设备只能接入您的APP

---

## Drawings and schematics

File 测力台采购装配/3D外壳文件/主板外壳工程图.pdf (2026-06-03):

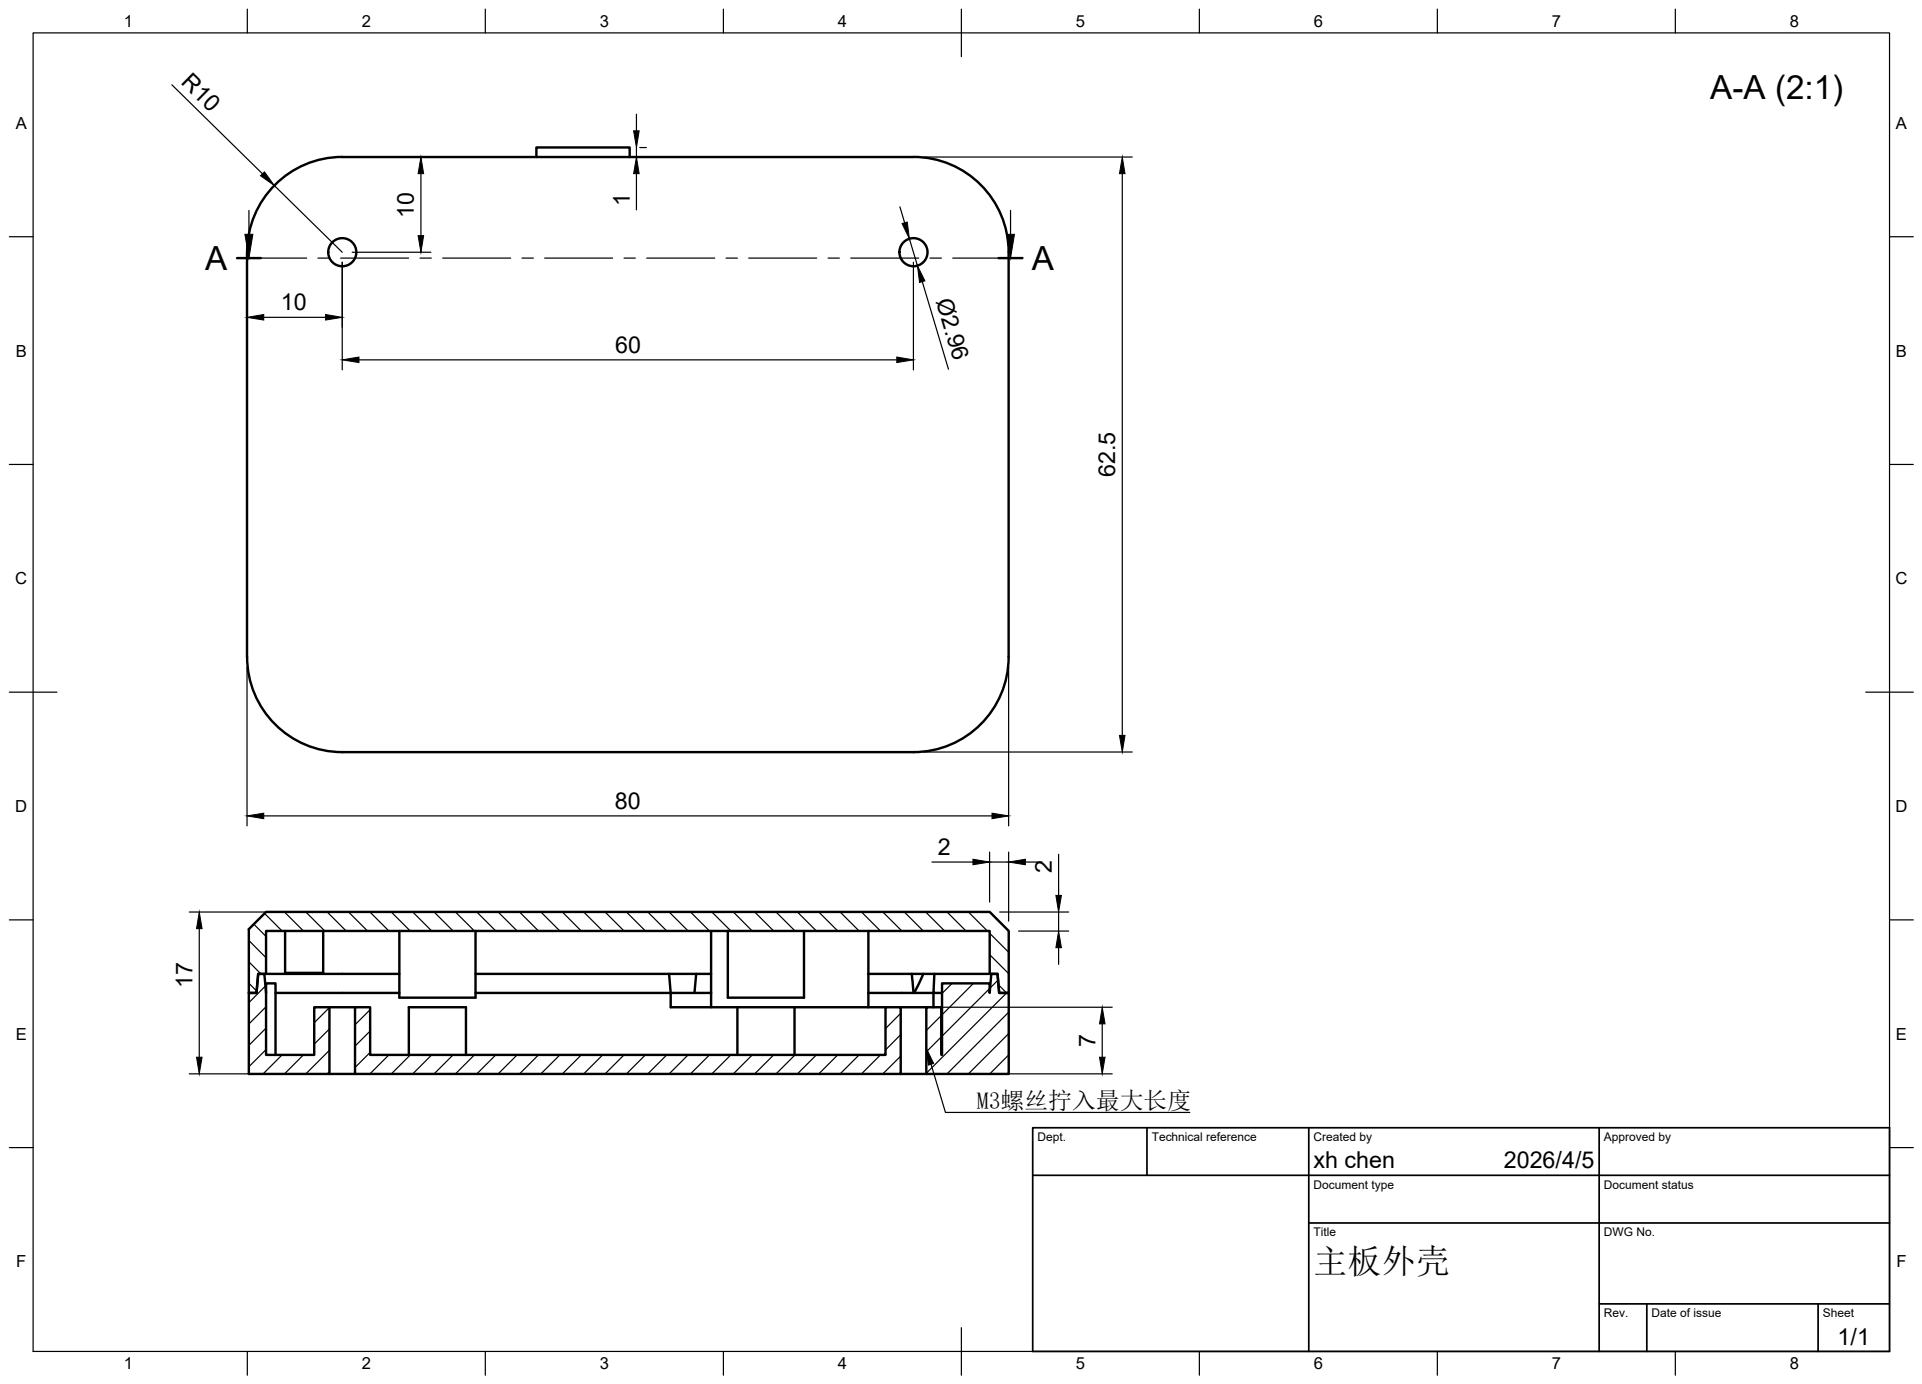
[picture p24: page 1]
Title; DWG No.; Rev.; Date of issue; Sheet

Dept. | Technical reference | Created by xh chen 2026/4/5 | Approved by

Document type | Document status

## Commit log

2026-04-06 Rename 3D_PCB5_1_2026-04-03 工程图 v6_01.png to PCB5_工程图.png
2026-04-06 update 工程图
